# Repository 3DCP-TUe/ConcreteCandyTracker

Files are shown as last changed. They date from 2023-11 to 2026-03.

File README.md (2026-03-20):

# Concrete Candy Tracker
  
<p align="left"> 
  
  
  
  
</p>

Concrete Candy Tracker is a software package developed for conducting tracer experiments in concrete processing. The experiment is described in detail in the paper titled "[An in-line dye tracer experiment to measure the residence time in continuous concrete processing](https://link.springer.com/article/10.1617/s11527-024-02378-y)". 

The tool includes software for data acquisition and template files for analyzing the results, such as deriving residence time functions from the acquired data. The tracer experiment uses a digital image processing (DIP) technique to detect a dye or pigment used as tracer material. The name originates from the dye Rhodamine B, which was initially used during the development of the experiment, as it stained the concrete with a candy cane–like effect.

## Hardware requirements

The software is optimized for use with the following hardware components at TU/e:

- Industrial camera: Basler a2A1920-51gcPRO
- Lens: Edmund Optics 16MM Compact Fixed Focal Length
- UV protection filter: Midwest Optical AC400
- Polarization filter: Midwest Optical PR032-25.5
- Polarized brick light: PL-ELSB-105SW
- Bandpass filter: Midwest Optical Bi550 (optional)

If a different Basler camera is used, the camera class may need to be adjusted. The listed bandpass filter is suitable for Rhodamine B. However, if you are using a different tracer material, you will need to select the appropriate bandpass filter for it.

## Installation

### Python

The current release is tested with Python 3.8 and requires the following libraries:

- The official Python wrapper for the camera from Basler: [PyPylon](https://www.baslerweb.com/en-us/software/pylon/pypylon/)
- To set up an OPC UA server or to write to an OPC UA server: [opcua-asyncio](https://github.com/FreeOpcUa/opcua-asyncio)
- For numerical operations: [numpy](https://numpy.org/)

Additionally, install the [Pylon Viewer](https://www.baslerweb.com/en-us/software/pylon/pylon-viewer/) for visual verification of the region of interest (ROI), calibrating the orientation of the polarization filter and optimization of the network settings.

### Node-RED

[Node-RED](https://nodered.org/) is optional but recommended for creating a simple live dashboard. Install Node-RED along with the following packages:

- [node-red-contrib-opcua](https://flows.nodered.org/node/node-red-contrib-opcua)
- [node-red-dashboard](https://flows.nodered.org/node/node-red-dashboard)

You can start Node-RED by typing `node-red` in the command window and access it at:

- Flow management: http://localhost:1880/
- Dashboard view: http://localhost:1880/ui

## Explanation of the files

### Data acquisition

Files related to data acquisition are located in the **[src/acquisition/](src/acquisition/)** directory and include the following files and folders:

- **[src/acquisition/camera.py](src/acquisition/camera.py):** This file contains the camera class, which provides the implementation for interfacing with an industrial camera using the pypylon library. It includes methods for initializing the camera, capturing images, and managing camera settings. 
- **[src/calibration_auto.py](src/acquisition/calibration_auto.py):** This file is used for autmomatic calibrating the camera. You need to run this script with reasonable starting values. Once you have obtained your settings, make sure to copy them to the script you used for experiments.
- **[src/acquisition/calibration_manual.py](src/acquisition/calibration_manual.py):** This file is used for manually calibrating the camera. You need to run this script and adjust the settings to achieve the target color values. This process typically involves multiple runs and adjustments to fine-tune the settings. For detailed instructions on the calibration procedure, see the section "Calibration Procedure". Once you have finalized the procedure and obtained the settings, make sure to copy them to your script used for experiments.
- **[src/acquisition/opcua_local_server.py](src/acquisition/opcua_local_server.py):** Sets up a local OPC UA server, captures color values, and makes them available for external access.
- **[src/acquisition/opcua_remote_server.py](src/acquisition/opcua_remote_server.py):** Connects to an external OPC UA server, captures color values, and writes them to the server (e.g., an industrial PLC).
- **[src/acquisition/node-red/local_server_dashboard.json](src/acquisition/node-red/local_server_dashboard.json):** A simple dashboard for Node-RED, displaying real-time color values from the local OPC UA server.
- **[src/acquisition/node-red/remote_server_dashboard.json](src/acquisition/node-red/remote_server_dashboard.json):** A simple dashboard for Node-RED, displaying real-time color values from the remote OPC UA server.

### Data analysis

Files related to data analysis are located in the **[src/analysis/](src/analysis/)** directory and include the following files and folders:

- **[lib](src/analysis/lib):** MATLAB library containing standardized functions.
- **[rtd.m](src/analysis/rtd.m):** MATLAB script to extract the residence time distribution and its properties from the acquired data.

The analysis files provided in this folder should be considered as templates and are fully functional with the latest version of the CSV format. You can use these files for data analysis or to quickly gain insights into your data. Store these files together with your dataset and adjust them if needed. If you add new functionality or create new templates please push these updates to this repository so that others can also benefit from them.

## Camera Network Connection (GigE Optimization)

To ensure reliable and high-performance image acquisition from a Basler GigE camera, follow these steps:

1. Enable Jumbo Frames on the used network adapter (if supported):
   - Open the **Device Manager**
   - Go to **Network Adapters**, right-click the Ethernet adapter used, select **Properties**
   - In the **Advanced** tab, find the property labeled "**Jumbo Frame**" or "**Jumbo Packet**" and set it to 9014 bytes (or maximum available value)
   - Click **OK** and restart the network interface

2. Optimize bandwidth settings in Pylon Viewer
   - Open **Pylon Viewer**
   - Connect to your camera
   - Open the [**Bandwidth Manager**](https://docs.baslerweb.com/bandwidth-manager)
   - Select your camera and run the optimization process
   - After optimization, close the **Bandwidth Manager**
   - Go to the **Transport Layer** settings
   - Note the values set for **Packet Size** and **Inter-Packet Delay**
   - Apply the values for **Packet Size** and **Inter-Packet Delay** in your Python script using the appropriate methods on the Camera instance: `set_packet_size` and `set_inter_packet_delay`

**Note**: You may need to re-adjust these values if you change network cables, adapters, or other system hardware, as optimal settings can vary.

## Calibration procedure/checklist

Mounting:

- Mount the camera, lens, and polarized light source.
- Place the camera 100 mm away from the concrete surface (this is the distance between the object and the lens without filters).
- Set the focus length of the lens to 0.1 m.
- Set the aperture of the lens at f/8.
- Mount the UV protection filter.
- Mount the polarization filter.
- Clean the light source and the lens.

Orientation:

- Orient the polarization filter correctly. Verify this by placing a piece of wet concrete in front of the lens: use a piece of hardened concrete and drip a bit of water on it. Rotate the filter to the position in which no glare is visible. Pylon Viewer can assist in this step.

Configuration:

- Set the region of interest (ROI). Verify the ROI with the Pylon Viewer.
- Set the exposure time at 16000.

White Balance Calibration:

- Run the data acquisition for at least one hour to heat the light source and camera. Do this for the calibration procedure and before you perform the experiment.
- Calibrate the white balance with an 18% grey card. For this step, you can use the `calibrate` function in the `Camera` class or adjust the values manually. For the latter, run the data acquisition for a short time each iteration (e.g., acquire 100 images). The goal is to set all linear RGB color values at 46. Adjust the gain value to scale all linear RGB color values. If values are below 46, increase the gain; if above 46, lower the gain. To obtain equally balanced color values: Set the white balance ratio R to 1.0. Adjust the white balance ratio G and B to obtain equal linear RGB color values of 46. If the color value G is below the color value R, increase the white balance G; if the color value G is above the color value R, decrease the white balance ratio G. Do the same for color value B. Note that changing the white balance G and B will affect all color values. Conduct several iterations with small adjustments to achieve linear RGB values of 46. Typical white balance ratios at TU/e are around 1.0, 0.545, and 1.257 for R, G, and B, respectively. Typical gain values are around 2.5-3.0, depending on the position of the light source.

White Point Measurement:

- Measure the white point by placing a white card in front of the lens. Acquire images for a short time (e.g., 100 images). The CIEXYZ color values represent the white point. As a reference, the values for daylight (D65) are 0.9504, 1.00, and 1.0888. Typical white point reference values at TU/e are 0.938, 0.981, and 1.070.
- Finally, set the measured white point values in the camera class. The white point is used to transform the color values from linear RGB color space to CIELAB color space.
If all steps are performed correctly, the measured CIELAB color values of an 18% grey card should come close to 50, 0, 0 for L*, a*, and b*, respectively.

Additional steps in case a bandpass filter is used:

- Remove the polarization filter and UV filter.
- Mount the bandpass filter.
- Reattach the polarization filter.
- Ensure the polarization filter is in the correct orientation.
- Recalibrate the gain value with an 18% grey card. Adjust the gain value to scale the L* value of the CIELAB color space to 50%. Use the already measured white reference point for this step.

Store your setup information and calibrated values:

- Store the information about the used setup, along with the data from the experiment. A template metadata file with the calibrated values, as well as the used hardware and software, is provided [here](database_template/setupinfo/metadata.yml). 
- After calibration, make short measurements (e.g., 60 seconds) on the grey and white card and store these as well. 

## Version numbering
Concrete Candy Tracker uses the following [Semantic Versioning](https://semver.org/) scheme: 

```
0.x.x ---> MAJOR version when you make incompatible API changes
x.0.x ---> MINOR version when you add functionality in a backward-compatible manner
x.x.0 ---> PATCH version when you make backward-compatible bug fixes
```

## How to cite

The in-line tracer experiment is fully detailed in its corresponding journal paper. Please use this paper as a reference for the developed tracer experiment. The BibTeX entry is provided below:

```bibtex
@article{Deetman2024,
  author = {A. Deetman and D. Bos and J. Blaakmeer and T. Salet and S. Lucas},
  title = {An in-line dye tracer experiment to measure the residence time in continuous concrete processing},
  journal = {Materials and Structures},
  volume = {57},
  number = {104},
  year = {2024}
  doi = {10.1617/s11527-024-02378-y},
}
```

Concrete Candy Tracker is a software toolkit that implements these tracer experiments. We kindly ask you to cite it if used or built upon. For general references to this software package, the Zenodo record can be cited. The BibTeX entry is provided below:

```bibtex
@misc{ConcreteCandyTracker_Zenodo,
    title = {{C}oncrete {C}andy {T}racker: {A} software toolkit for tracer experiments in concrete processing},
    author = {A. Deetman and D. Bos},
    publisher = {Zenodo},
    year = {2025},
    doi = {10.5281/zenodo.17277859},
    note = {Zenodo. doi:10.5281/zenodo.17277859}
}
```

On our [Zenodo page](https://doi.org/10.5281/zenodo.17277859), you can find how to cite specific versions of the software.

## Funding

This software could be developed and maintained with the financial support of the following projects:
- The project _"Additive manufacturing of functional construction materials on-demand"_ (with project number 17895) of the research program _"Materialen NL: Challenges 2018"_ which is financed by the Dutch Research Council (NWO).

## Contact information

If you have any questions or comments about this project, please open an issue on the repository’s issue page. This can include questions about the content, such as missing information, and the data structure. We encourage you to open an issue instead of sending us emails to help establish an open community. By keeping discussions open, everyone can contribute and see the feedback and questions of others. In addition to this, please see our open science statement below.

## Open science statement

We are committed to the principles of open science to ensure that our work can be reproduced and built upon by others, by sharing detailed methodologies, data, and results generated with the unique equipment that is available in our lab. To spread Open Science, we encourage others to do the same to create an (even more) open and collaborative scientific community. 
Since it took a lot of time and effort to make our data and software available, we license our software under the General Public License version 3 or later (free to use, with attribution, share with source code) and our data and documentation under CC BY-SA (free to use, with attribution, share-alike), which requires you to apply the same licenses if you use our resources and share its derivatives with others. 

## License

Copyright (c) 2023-2025 [3D Concrete Printing Research Group at Eindhoven University of Technology](https://www.tue.nl/en/research/research-groups/structural-engineering-and-design/3d-concrete-printing)

Concrete Candy Tracker is free software; you can redistribute it and/or modify it under the terms of the GNU General Public License version 3.0 as published by the Free Software Foundation. 

Concrete Candy Tracker is distributed in the hope that it will be useful, but WITHOUT ANY WARRANTY; without even the implied warranty of MERCHANTABILITY or FITNESS FOR A PARTICULAR PURPOSE. See the GNU General Public License for more details.

You should have received a copy of the GNU General Public License along with Concrete Candy Tracker; If not, see <http://www.gnu.org/licenses/>.

@license GPL-3.0 <https://www.gnu.org/licenses/gpl-3.0.html>

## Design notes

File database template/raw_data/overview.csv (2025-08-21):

experiment | serie | input | component | inlet | time_start | time_end
1 | 1 | impulse | mai multimix-1 | injection port at start of horizontal mixer | 09:50:51 | 10:25:51

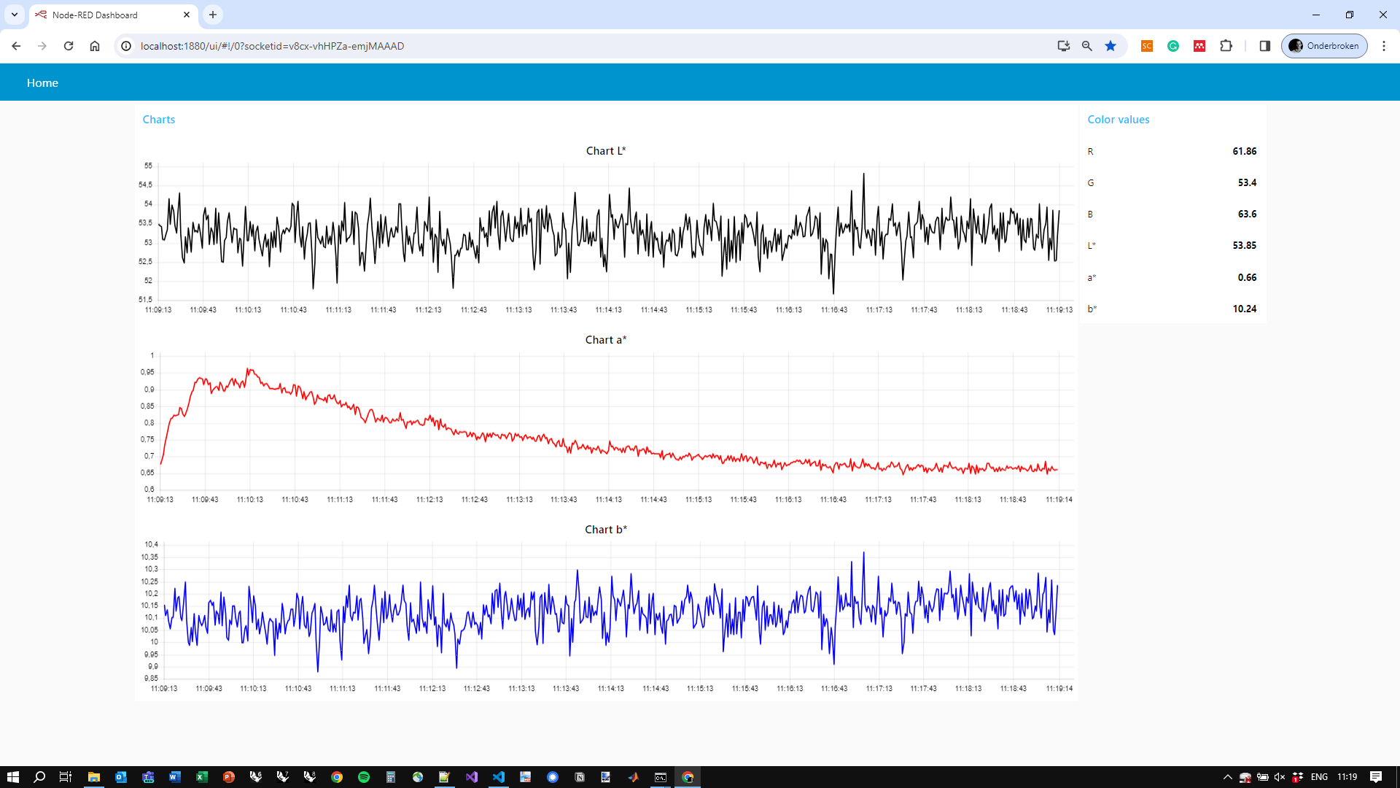
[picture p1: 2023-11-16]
utils/images/node-red-dashboard.png

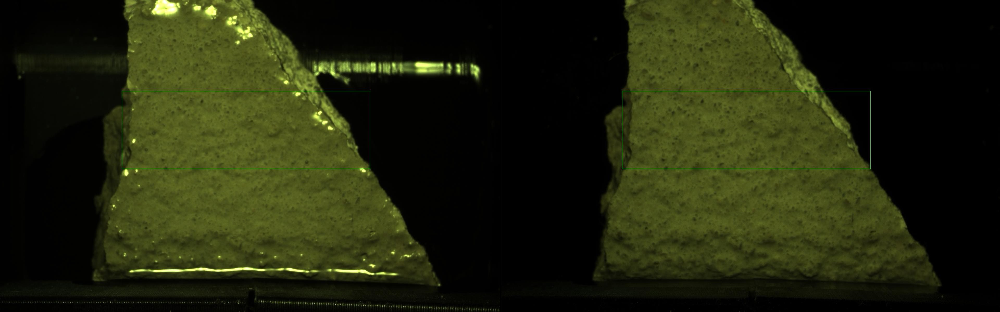
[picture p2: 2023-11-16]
utils/images/polarization_filter.jpg

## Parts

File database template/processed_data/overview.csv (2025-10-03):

experiment | serie | input | material_component | system_component | system_component_inlet | size | time_start | time_end | file_name | mean | variance | std | p1 | p5 | p50 | p95 | p99
1 | 1 | impulse | pigment slurry | mai multimix-1 | injection port at start of horizontal mixer | 15 | 09:50:51 | 10:25:51 | response_1.csv | 00:11:58 | 22:59:23 | 00:04:47 | 00:06:45 | 00:07:21 | 00:10:25 | 00:22:21 | 00:30:44

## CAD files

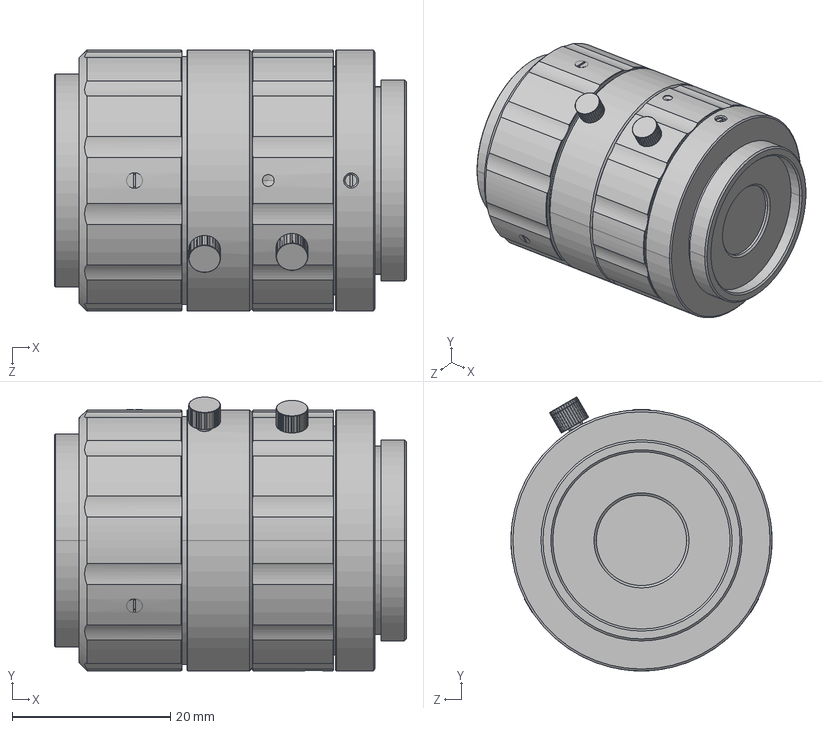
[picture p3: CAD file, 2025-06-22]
database template/setupinfo/docs/lens/Edmund_Optics_3d_model.step
44.5 x 34.6 x 33.0 mm

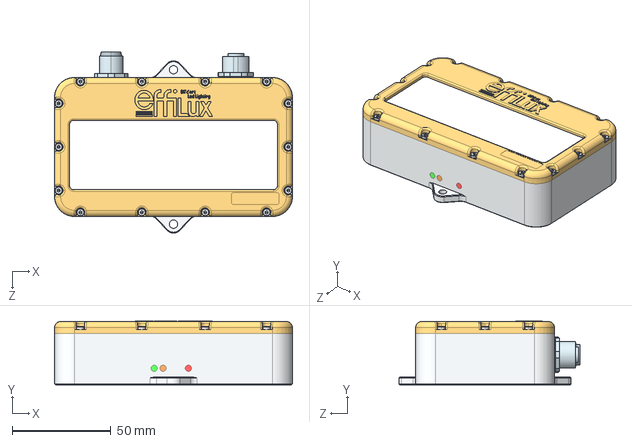
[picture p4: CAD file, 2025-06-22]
database template/setupinfo/docs/light/ELSB-105_3d_model.STEP
120.2 x 32.2 x 91.5 mm

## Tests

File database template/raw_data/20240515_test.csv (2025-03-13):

Time | R | G | B | X | Y | Z | L* | a* | b*
09:26:40.469 | 0.004 | 0.000 | 0.001 | 0.000007 | 0.000004 | 0.000002 | 0.009250 | 0.027833 | 0.007904
09:26:40.486 | 0.004 | 0.000 | 0.001 | 0.000008 | 0.000005 | 0.000003 | 0.009880 | 0.030301 | 0.007784

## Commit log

2023-11-20 Improved the python files: constants, logging...
    [test.csv]
2023-11-20 Fixed the camera event handlers
2024-04-29 Add method to the camera class to get if the camara is grabbig
2024-04-30 Update camera ip address
2024-05-06 Latest calibration values
2024-05-07 Added the grab average method to the camera class
2024-05-14 Update test.csv log file
    [test.csv]
2024-07-18 Improved the docstrings of the Camera class
2024-07-18 Added a simple file that can be used for camera calibration
2024-08-10 Added an example of a metadata file
    [20240515_test.csv]
2024-08-12 Added the save_image method to the camera class
2024-08-20 Updated the folder structure
    [20240515_test.csv]
2025-02-21 Remove database template
    [20240515_test.csv]
2025-03-13 Added the database template
    [20240515_test.csv, color_values.csv]
2025-05-19 Fixed missing reference to database variable in calibration file
2025-05-20 Renamed calibration file
2025-05-20 Added color calibration methods
2025-05-20 Added a example files that used the calibration functions
2025-05-20 Updated calibration parameters
2025-05-20 Renamed the method calibrate to color_calibration
2025-06-22 Add docs to database template
    [ELSB-105_3d_model.STEP, Edmund_Optics_3d_model.step]
2025-08-21 Update database template
    [overview.csv, rtd_1.csv]
